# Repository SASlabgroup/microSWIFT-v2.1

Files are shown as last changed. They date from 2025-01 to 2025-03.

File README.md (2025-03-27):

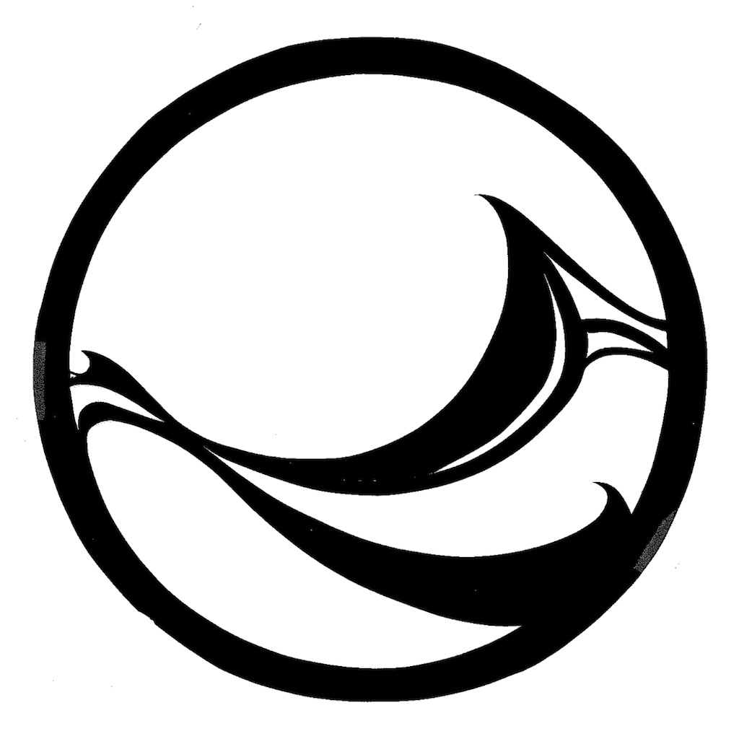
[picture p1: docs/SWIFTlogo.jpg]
#  microSWIFT v2.1

Static repository for documentation, source code, and CAD files for version 2.1 of the microSWIFT wave buoy.

## About microSWIFT
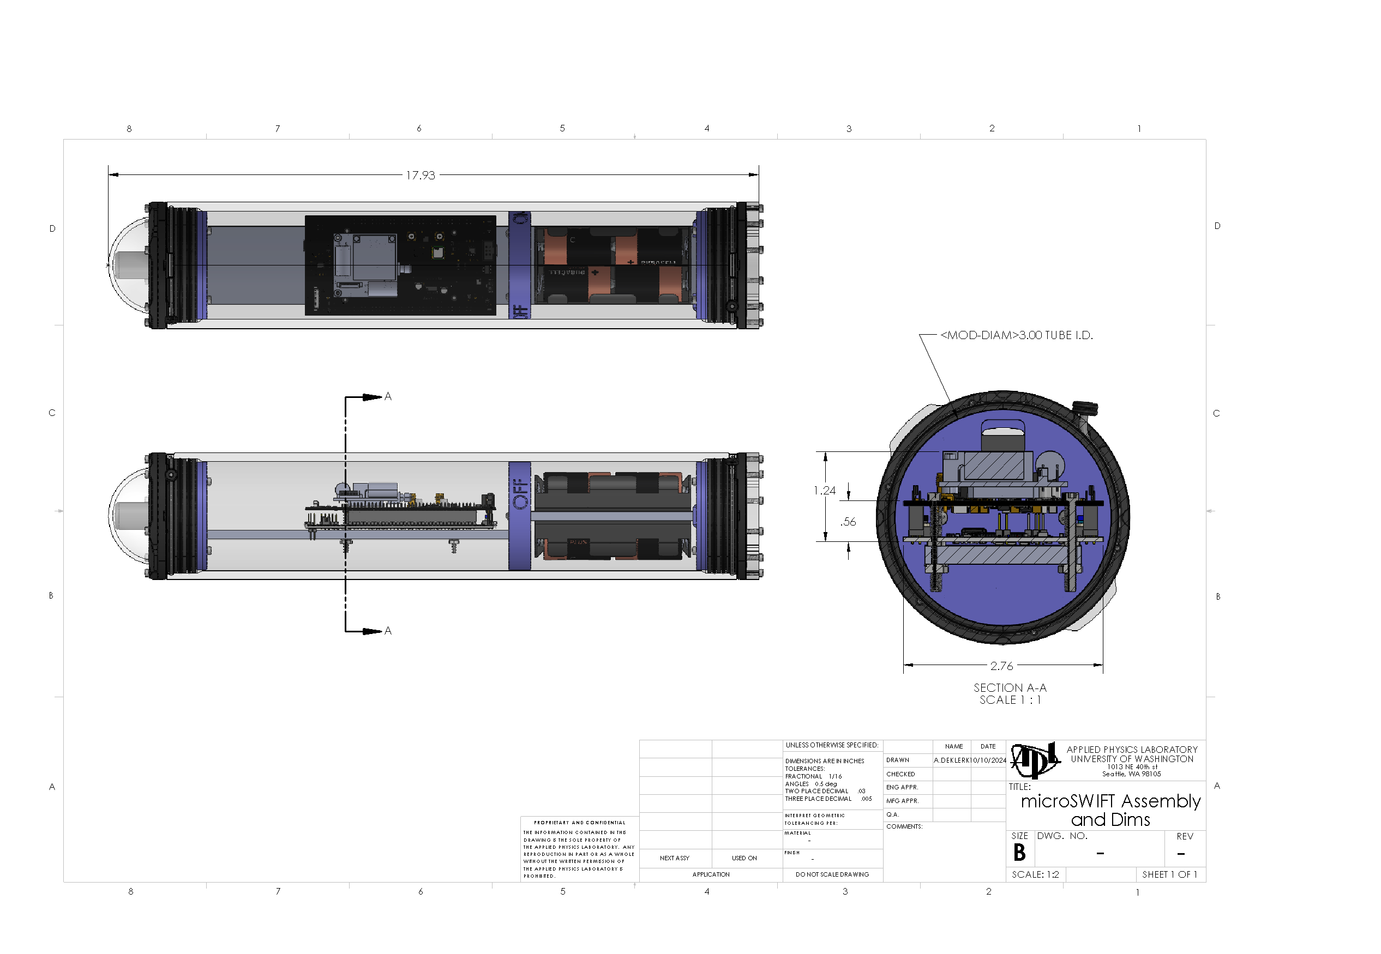
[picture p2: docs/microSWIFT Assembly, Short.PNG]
# 
microSWIFT is a low-cost, expendable, freely drifting wave buoy built by at the UW Applied Physics Lab.  It uses the Iridium satellite network to report real-time ocean wave data. It also supports additional measurements such as surface salinity and temperature via auxiliary sensors.

microSWIFT can be deployed from an aircraft through a standard A-size Sonobuoy tube.  This makes it ideal for collecting wave data in environments not accessible by ship, such as in the path of a hurricane or in polar regions.  It can also be deployed by hand over the side of a ship like a traditional buoy or drifter.

The name microSWIFT owes to the fact that it is a miniaturized version of a SWIFT wave drifter.  SWIFT is an acronym for Surface Wave Instrument Float with Tracking.

Visit the main APL project page for more information: https://apl.washington.edu/swift

Database (real time and archive) is available here: https://faculty.washington.edu/jmt3rd/SWIFTdata/DynamicDataLinks.html

A full Python package for working with microSWIFT  telemetry data is available as a separate repository: 
https://github.com/SASlabgroup/microSWIFTtelemetry

The microSWIFT v2 onboard software is here: https://github.com/SASlabgroup/microSWIFT-V2

## microSWIFT v1
The first version of the microSWIFT was based on a Raspberry Pi Zero and ran on Python code.  Documentation and operational code can be found a the microSWIFT v1 repo: 
https://github.com/SASlabgroup/microSWIFT

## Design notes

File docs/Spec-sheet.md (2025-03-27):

# Specs and Features

# 
## General Specifications

|                                       |                                                |
|:------------                          |:-----------------------------------------------|
|Enclosure                              |Acrylic watertight housing (120 m depth rating)
|Buoy dimensions                        |3.5 in diameter, 17.9 in length
|Weight                                 |6 lbs
|Air-drop package                       |Cardboard tube with 28” diameter chute
|Air-drop dimensions                    |4.25” diameter, 25.5” length,
|Air-drop weight                        |8 lbs (including buoy)
|Batteries                              |8 standard Alkaline “C” cells, user replaceable
|Endurance                              |21 days
|Telemetry                              |Satellite (Iridium SBD), 9603 modem
|Processor                              |STM32U5 series (ARM® Cortex®-M33) , 768 kB RAM, 2048 kB Flash memory
|Onboard software                       |C (https://github.com/SASlabgroup/microSWIFT-v2.1-source)
|Duty cycle                             |Configurable.  Typically 30 minute interval for collection of raw wave data (GPS at 4 Hz), onboard processing, and telemetry.  
|Optional sensors                       |Conductivity and temperature (CT) sensor
|Optional long endurance configuration  |16x C cell batteries in extended housing

## Data Products
|                                                     |                                                |
|:------------                                        |:-----------------------------------------------|
|Position (lat, lon)                                  |± 5 m
|Significant wave height, Hs                          |± 0.1 m
|Peak wave period, Tp                                 |± 1 s
|Dominant wave direction, Dp                          |± 15 deg
|Scalar wave energy spectrum, E(f)                    |± 10-2 m2/Hz, 0.05 < f < 0.5 Hz
|Directional moments of the spectrum (a1,a2,b1,b2)    |± 0.1, 0.05 < f < 0.5 Hz

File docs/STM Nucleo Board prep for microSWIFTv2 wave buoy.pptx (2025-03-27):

## STM NUCLEO Board prep for microSWIFT v2 wave buoy

(NUCLEO-U575ZI-Q)
Alex de Klerk, Aug 2023

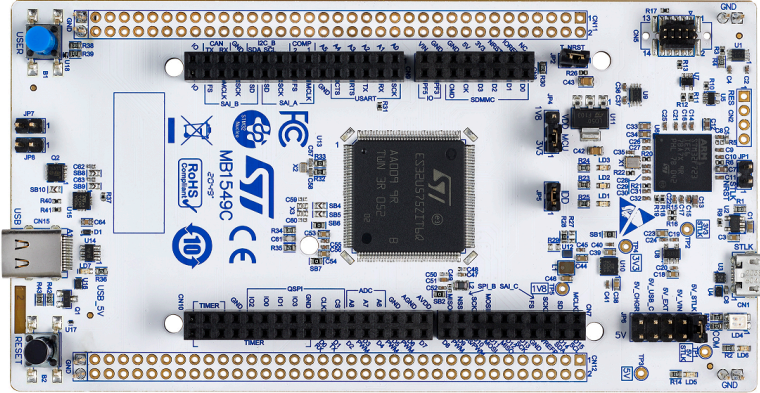
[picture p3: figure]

## Follow ESD safe practices while handing electronic circuit board and components

- Use an ESD safe work mat that is grounded
- Wear grounding strap
- Store board in factory anti-static bag

## 1) Flush cut header pins

- Remove board from packaging
- Use good flush cutters (Knipex or similar)
- Trim header pins on bottom side of board flush with board (red boxes)
- Be careful not to damage silk screen or traces

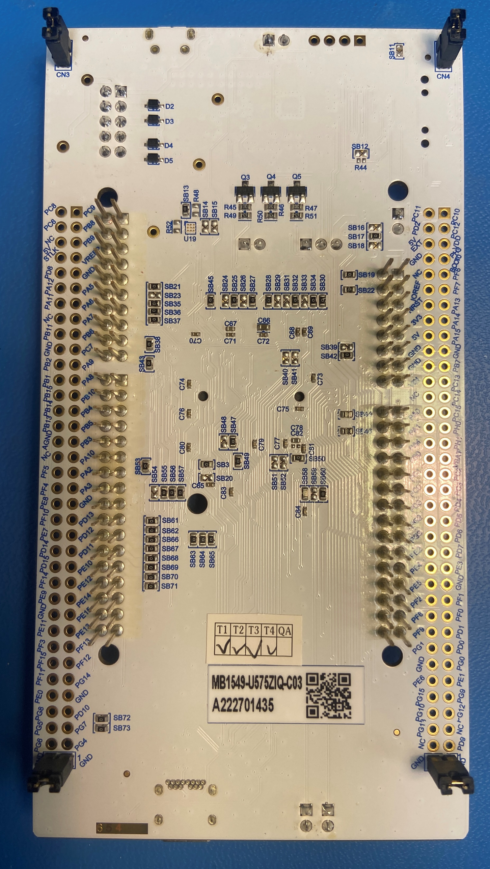
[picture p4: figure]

## 2) Solder male header pins

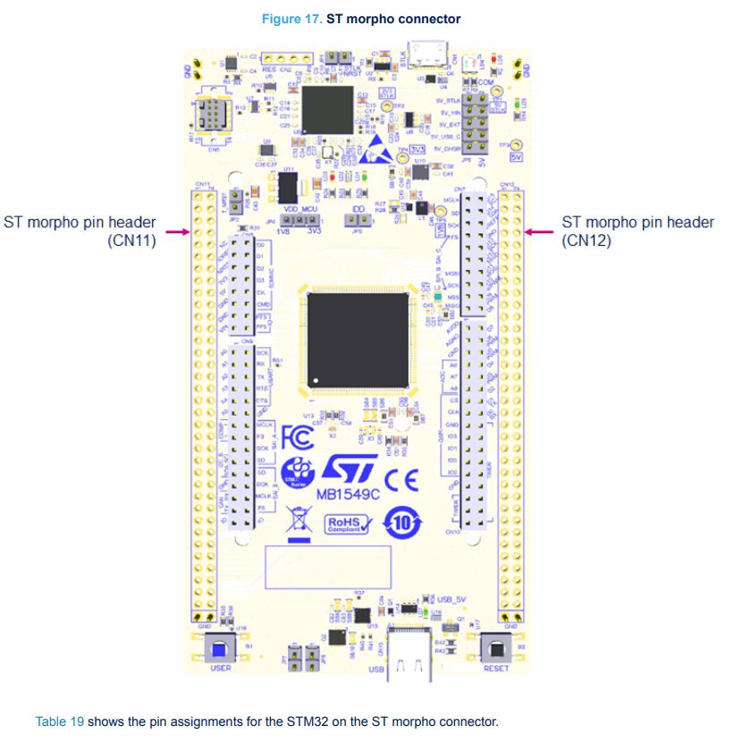
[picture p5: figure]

- Use 2x35 male header pins, qty 2
- Solder on top side of board in MORPHO locations (outer 4 rows) as shown below
- Use flux and make sure flows between pad and header pin

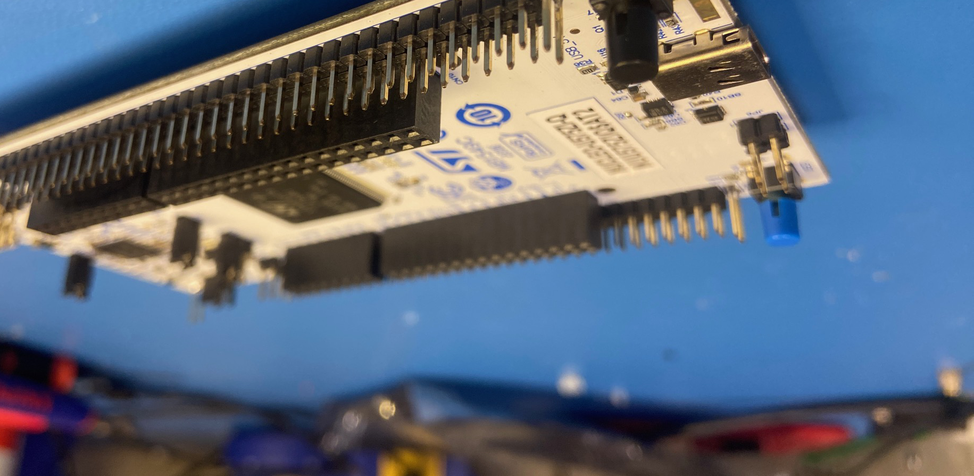
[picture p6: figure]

## 3) De-populate SB1

- Remove 0 Ohm resistor from SB1 location
- Use solder wick and flux to remove excess solder

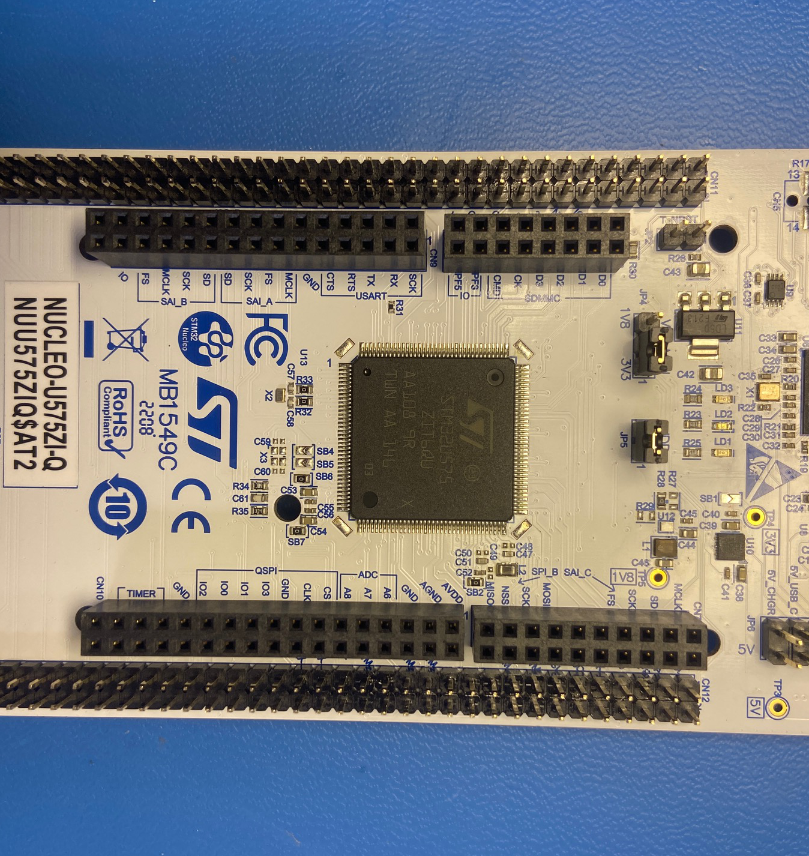
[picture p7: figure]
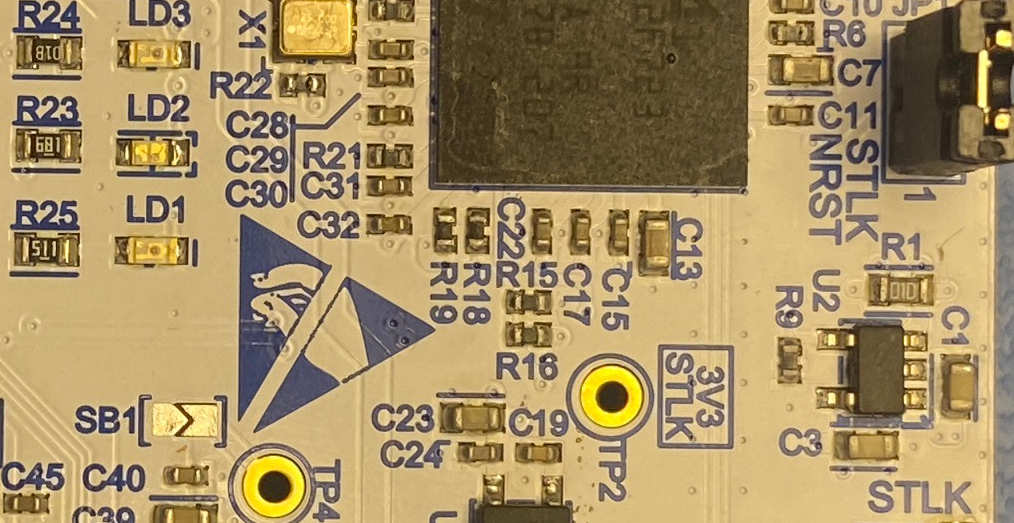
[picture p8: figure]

SB1

## 4) De-populate SB3

- Remove 0 Ohm resistor from SB3 location (bottom side)
- Use solder wick and flux to remove excess solder

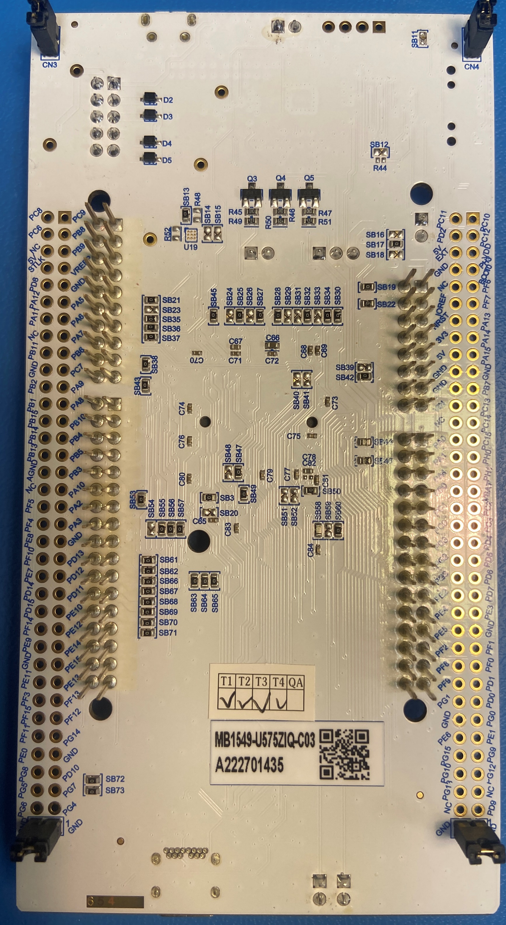
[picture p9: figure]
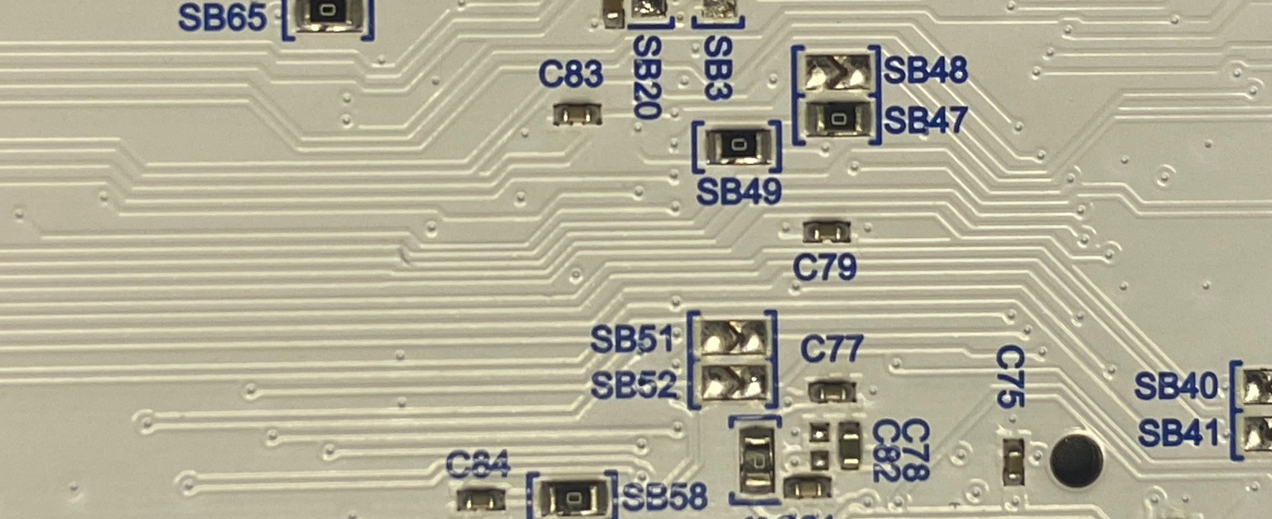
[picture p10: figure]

SB3

## Set Jumpers

- Remover jumper JP6
- Remove jumper JP2
- Install jumper at JP1

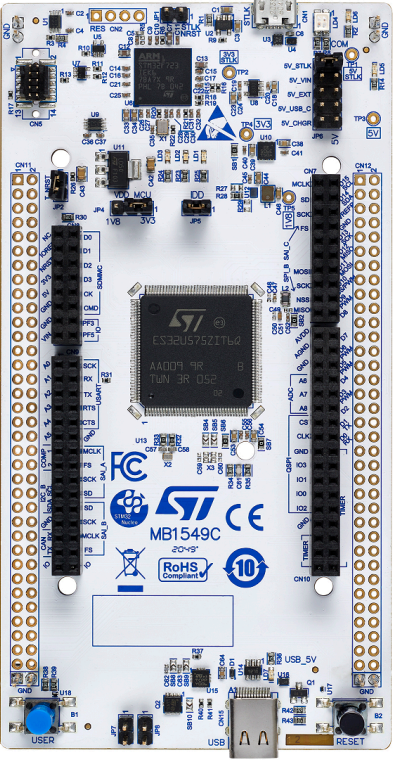
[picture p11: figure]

## 5) Clean flux from board

- Use isopropyl alcohol (IPA) in a squirt bottle and a stiff brush (ESD safe preferable)
- Wet board with IPA and scrub flux at all solder locations, SB1, and SB3
- Rinse and scrub several times
- Final rinse and air dry with canned compressed air

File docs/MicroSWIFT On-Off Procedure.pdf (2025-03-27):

# MicroSWIFT On/Off Procedure

## To Turn on the microSWIFT

The microSWIFT can be turned on by placing a magnet wand or other magnet near the location marked ‘ON’ for 1-3 seconds. The magnet sensor is located in the bottom right corner of the circuit board.

When powered on, a red and green status LEDs will alternately flash while the microSWIFT boots up. After approximately 1 minute, there should be a solid green LED, indicating the microSWIFT has started running successfully.

During operation, there will be a solid green LED while the buoy is collecting data, otherwise both status LEDs will be off.

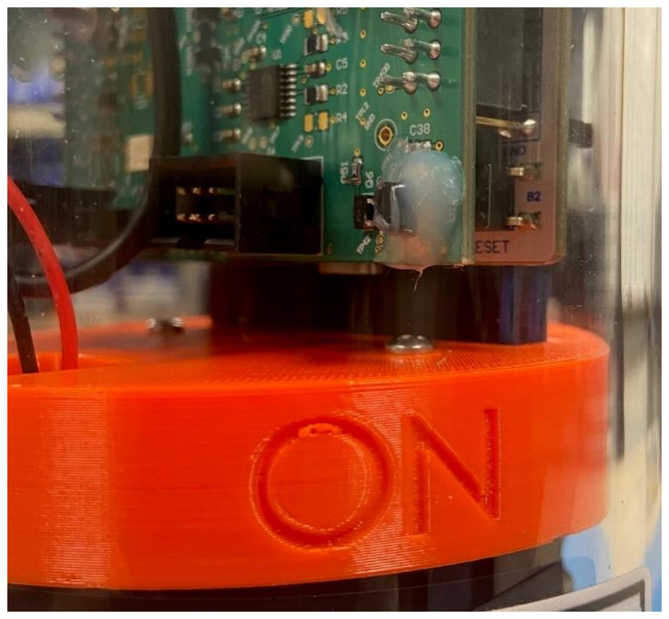
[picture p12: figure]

## To Turn off the microSWIFT

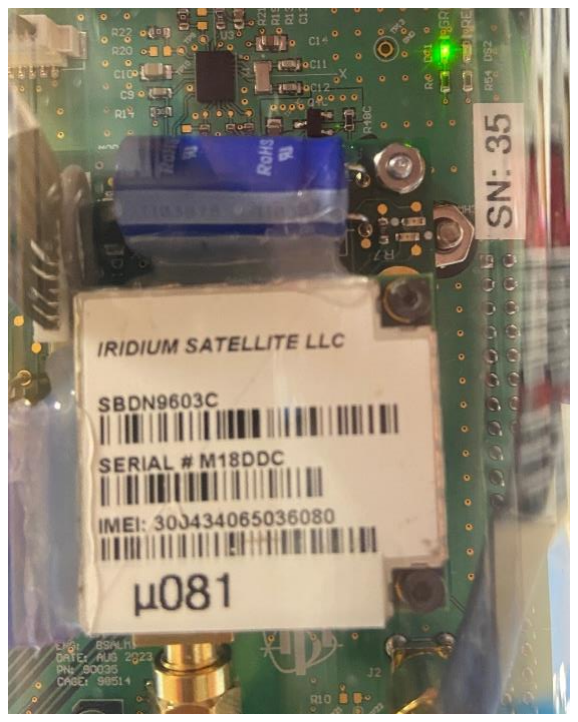
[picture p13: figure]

Place the magnet wand or another magnet near the location marked ‘OFF’. The status LEDs will turn off, however the LEDs on the Iridium modem will turn on as its capacitor discharges.

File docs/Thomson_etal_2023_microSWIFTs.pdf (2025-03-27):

Full Terms & Conditions of access and use can be found at https://www.tandfonline.com/action/journalInformation?journalCode=tcej20

Jim Thomson, Phil Bush, Viviana Castillo Contreras, Nate Clemett, Jacob

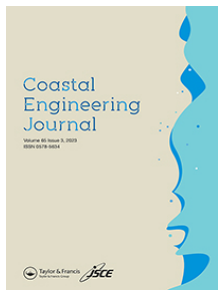
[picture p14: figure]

Davis, Alex de Klerk, Emily Iseley, Edwin James Rainville, Brenton Salmi & Joe Talbert (22 Nov 2023): Development and testing of microSWIFT expendable wave buoys, Coastal Engineering Journal, DOI: 10.1080/21664250.2023.2283325 (https://www.tandfonline.com/action/showCitFormats?doi=10.1080/21664250.2023.2283325)
https://doi.org/10.1080/21664250.2023.2283325

© 2023 The Author(s). Published by Informa UK Limited, trading as Taylor & Francis Group.

Published online: 22 Nov 2023.

Submit your article (https://www.tandfonline.com/action/authorSubmission?journalCode=tcej20&show=instructions) to this journal

View related (https://www.tandfonline.com/doi/mlt/10.1080/21664250.2023.2283325) articles

View Crossmark (http://crossmark.crossref.org/dialog/?doi=10.1080/21664250.2023.2283325&domain=pdf&date_stamp=22%20Nov%202023) data

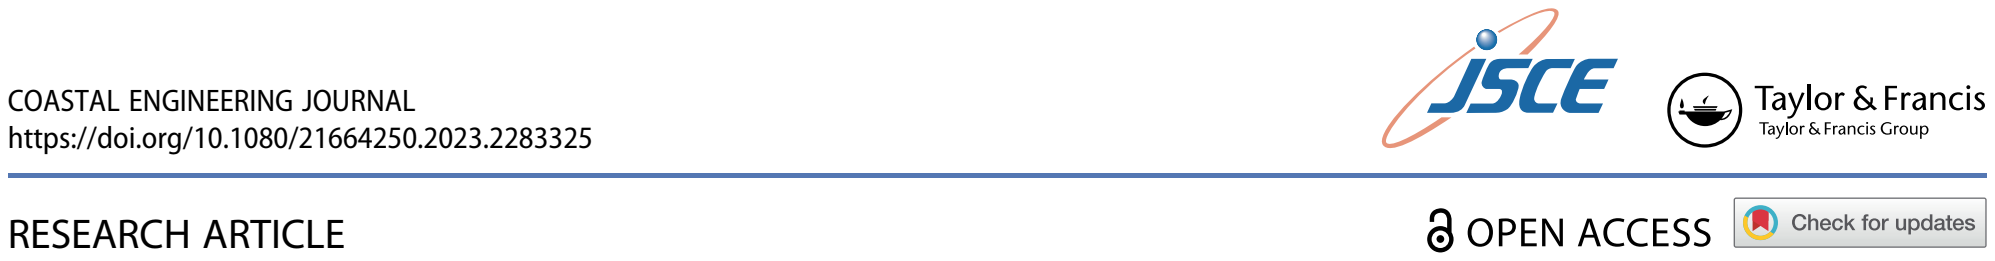
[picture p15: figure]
RESEARCH ARTICLE; COASTAL ENGINEERING JOURNAL https://doi.org/10.1080/21664250.2023.2283325

## Development and testing of microSWIFT expendable wave buoys

Jim Thomson , Phil Bush, Viviana Castillo Contreras, Nate Clemett, Jacob Davis , Alex de Klerk, Emily Iseley, Edwin James Rainville , Brenton Salmi and Joe Talbert

Applied Physics Laboratory, University of Washington, Seattle WA, USA

ABSTRACT
Expendable microSWIFT buoys have been developed and tested for measuring ocean surface waves. Wave spectra are calculated via onboard processing of GPS velocities sampled at 5 Hz, and wave spectra are delivered to a shore-side server via Iridium modem once per hour. The microSWIFTs support additional sensor payloads, in particular seawater conductivity and temperature. The buoys have a non-traditional, cylindrical shape that is required for deployment via the dropsonde tube of research aircraft. Multiple versions have been developed and tested, with design considerations that include: buoy hydrodynamics, sensor noise, algorithm tuning, processor power, and ease of deployment. Field testing in a range of conditions, including near sea ice and in a hurricane, has validated the design.

ARTICLE HISTORY
Received 9 July 2023
Accepted 30 October 2023
Published online
KEYWORDS
Ocean surface waves; wave
buoy; wave measurements;
wave spectra

### 1. Introduction

The modern era of ocean wave measurements is de!ned by an expansion in operational remote sensing (e.g. satellite altimeters, lidar scanners) and by a "ood of inexpensive wave buoys (e.g. Spotter buoys, openMet buoys). Amidst the plethora of miniature wave buoys, one can and should ask if another wave buoy is needed. The answer is that speci!c projects often require unique features or sampling modes not available in existing buoy designs. Our development of microSWIFT buoys has been motivated by several speci!c projects needs, including: access to raw data for phase resolved models, high sampling rates for breaker detection, robustness in sea ice, aerial deployment from the dropsonde tube of research aircraft, and inclusion of additional sensors as modular payloads. Collins et al. (2024) provides a thorough review of wave buoy measurements and an inter-calibration e#ort for several miniature wave buoys. Much of this activity traces directly back to Herbers et al. (2012), who demonstrated the utility of Global Positioning System (GPS) Doppler velocities as the raw motion data for wave spectral analysis. This was a departure from the classic pitchroll-heave motion data (Kuik, Van Vledder, and Holthuijsen 1988), and thus the use of GPS data helped launch a new generation of wave buoys. The SWIFT buoys (Thomson 2012) immediately adopted the GPS approach, as did many other buoys and platforms (Raghukumar et al. 2019; Thomson et al. 2018). Other modern buoys have used newly available, low-cost Inertial Motion Unit (IMU) sensors (Feddersen et al. 2024; Rabault et al. 2020, 2022). The development of microSWIFT buoys has explored both GPS and IMU approaches, as part of a larger e#ort to miniaturize the original SWIFT design and end up with something compact and expendable.
The goal of this paper is to describe the development and testing of microSWIFT buoys, with particular attention to lessons learned that have steadily improved the quality of the wave data and the usability. Section 2 describes the design of the buoys, Section 3 describes the algorithms, Section 4 describes testing the buoys, and Section 5 summarizes the deployments to-date.

### 2. Buoy design

There have been three versions of microSWIFT buoys to date, each with a few variations. The !rst beta version was a simple proof-of-concept. Subsequent versions have evolved to address weaknesses identi!ed during testing and to address new mission requirements associated with new research projects. Figure 1 shows the di#erent physical designs, and Table 1 summaries the speci!cations. The choice of a cylindrical buoy shape throughout all versions, rather than the more common spherical buoy shape, is driven by a requirement for aerial deployments using the A-sized tube (nominal 5-inch diameter) for dropsondes from research aircraft, such as the NOAA P-3 Hurricane Hunter or Twin Otter.

CONTACT J. Thomson. jthomson@apl.washington.edu
© 2023 The Author(s). Published by Informa UK Limited, trading as Taylor & Francis Group.
This is an Open Access article distributed under the terms of the Creative Commons Attribution-NonCommercial-NoDerivatives License (http://creativecommons.org/licenses/bync-nd/4.0/), which permits non-commercial re-use, distribution, and reproduction in any medium, provided the original work is properly cited, and is not altered, transformed, or built upon in any way. The terms on which this article has been published allow the posting of the Accepted Manuscript in a repository by the author(s) or with their consent.

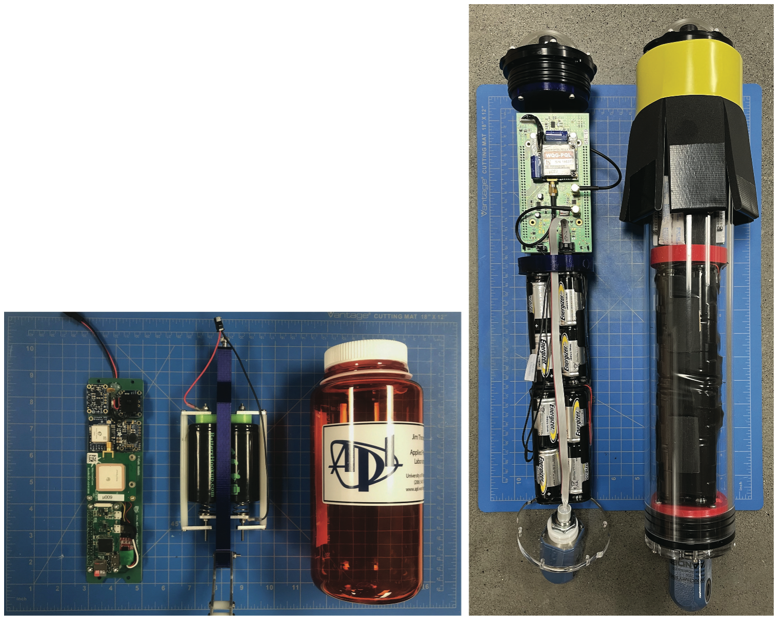
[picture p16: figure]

### 2.1. microSWIFT v-beta

The beta version of the microSWIFT buoy was simply a 1-Liter, Naglene-brand water bottle with two commercial, o#-the-shelf components: a GPS logger (Qstarz) and a dog-tracking collar (Garmin Astro). These were !rst deployed in 2014 to measure the wakes of Washington State Ferries in Rich Passage (Perfect et al. 2015), and later used for the DUNEX pilot in 2019. The endurance was approximately one day, and the system had no onboard processing or telemetry. The buoys had to be recovered (based on tracking with the dog collars) and the raw GPS data o$oaded for post-processing.

### 2.2. microSWIFT v1 (1-L and 2-L)

The !rst production version of the microSWIFT buoy still uses the 1-Liter Naglene bottle as the housing and upgrades the electronics to a RaspberryPi-0 processor on a custom Printed Circuit Board (PCB). This enables integration of a GPS receiver and IMU, with onboard processing and telemetry of results via Iridium modem. The RPi processor is an excellent choice for rapid, collaborative software development. A set of Python codes, managed in a public GitHub repo (https://github.com/SASlabgroup/microSWIFT) (https://github.com/SASlabgroup/microSWIFT) controls all aspects of data logging, processing, and telemetry. The RPi is also an excellent choice for short-deployments, because the WiFi connectivity can be used to automate the o$oad and organization of raw data from a large number of buoys (once recovered and in range of the network). This was helpful during the DUNEX main experiment, when up to 50 buoys were deployed on daily missions and post-processing raw data was essential (Rainville et al. 2023).
The RPi is a less ideal choice in terms of power usage. The v1 buoys use approximately 200 mW on-average, and most of this is the RPi itself (as opposed to the GPS, IMU, or Iridium modem). For the 1-L Naglene bottle housing with two D-cell rechargeable batteries, the maximum mission life is two days. A 2-L housing, based on Blue Robotics 3-inch inner diameter pressure

Figure 1. microSWIFT versions. Left: v1 in a 1-L Naglene bottle housing. Right: v2 in a 2-L housing (also used in a variation of v1) with an octopus foam collar. The 2-L version has an optional conductivity-temperature (CT) sensor at the bottom of the housing.

Table 1. microSWIFT versions.
Version | Processor | Endurance | Housing | Code base | Tracking/Telemetry | Unit Cost
beta | none | 1 day | 1-L Naglene | none | Dog collar/none | $250
v1 | RaspberryPi-0 | 2 days | 1-L Naglene | Python | Iridium | $500
v1 | RaspberryPi-0 | 5 days | 2-L Blue Robotics | Python | Iridium | $600
v2 | STM | 30 days | 2-L Blue Robotics | C | Iridium | $900*
*cost is increased by $2,000 with optional CT sensor.

2 J. THOMSON ET AL.

cases, provides space for 16 C-cell batteries and extends mission life to !ve days. This has been essential for successful deployments during the !rst year of the NOPP Hurricane Coastal Impacts (NHCI) program (see Section 5). The 2-L housing also includes a dedicated GPS antenna that improves the quality of the GPS velocities.

### 2.3. microSWIFT v2

The second production version of the microSWIFT replaces the RaspberryPi with a low-power microprocessor (STM32). This increases the endurance to approximately 30 days with the same 2-L housing and 16 Alkaline C-cell batteries. The increased endurance enables persistent observing that can capture events, especially in the western Arctic and in the tropical Atlantic pathway for hurricanes (see Section 5). The switch to a microprocessor includes a switch to C as the codebase and more specialized/intensive software development. Compared with the numerous Python libraries available for the RPi on v1, much of the C software for v2 had to be developed from scratch.
The v2 microSWIFT upgrades the GPS receiver to a multi-constellation GNSS unit (UBlox M10) which tracks up to 32 satellites at a time, compared with 16 GPS satellites tracked by most consumer grade GPS receivers. The additional satellites tracked are from the GALILEO, GLONASS, and BEIDOU constellations in orbit. The additional satellites improve the accuracy of the velocity components used as inputs to the onboard wave processing (Section 3), especially the vertical component of velocity. Errors in velocity components are expected to be <0:05 m/s. The v2 microSWIFT has a new PCB to integrate the microprocessor, GNSS receiver, and Iridium modem. Provisions for an IMU exist, though it is not included in the present onboard processing (see Section 3). There is also magnetic power switch, such that it can be turned on without opening the pressure case or the air-deployment rigging. The v2 microSWIFT also includes a conductivity and temperature (CT) sensor (Aanderaa 4319) at the bottom of the 2-L hull for determination of sea surface salinity and sea surface temperature (approximate measurement depth 0.2 m). This continues a general modular sensor approach used in the original full-scale SWIFTs, which have supported the same model CT for years (along with acoustic Doppler pro!lers, meteorological sensors, cameras, "uorometers, etc).

### 3. Onboard data processing

This section describes the microSWIFT onboard processing of GPS data to produce the standard ocean wave spectral and bulk metrics. Testing of the v1 microSWIFT included several iterations using the IMU data to produce similar metrics, as done on some other mini buoys (Feddersen et al. 2024; Rabault et al. 2020, 2022). Although post-processing the IMU data produced excellent results from the DUNEX project (Rainville et al. 2023), it has not been adopted as the standard for onboard processing. Two key problems have prevented the use of IMU data for onboard processing: 1) the correction from the body reference frame to the earth reference frame, and 2) the introduction of spurious energy at low frequencies when integrating motion data to estimate position. Both of these problems can be solved with su%cient computational power, !ltering, and calibration.
Rather than implement IMU sensor-fusion algorithms onboard or rely on black-box state estimates, we have chosen to use the GPS velocities exclusively in the onboard processing. These velocities are agnostic to buoy orientation and already in an earth reference frame, with orthogonal north-eastdown components (v; u; w). This approach is particularly well suited to non-spherical shapes that may not follow surface slopes. The processing uses the frequency spectra SÖfÜ of the components to estimate the scalar energy spectra,

## EÖfÜ à SuuÖfÜ á SvvÖfÜ

Ö2πfÜ

2 | (1)

and the standard directional moments,
a1ÖfÜ à | ImÖSuwÜ ÅÅÅÅÅÅÅÅÅÅÅÅÅÅÅÅÅÅÅÅÅÅÅÅÅÅÅÅÅÅÅÅÅÅÅÅÅÅÅÅÅÅÅÅÅÅ ÖSuuÖfÜ á SvvÖfÜÜSwwÖfÜ p | ;
b1ÖfÜ à | ImÖSvwÜ ÅÅÅÅÅÅÅÅÅÅÅÅÅÅÅÅÅÅÅÅÅÅÅÅÅÅÅÅÅÅÅÅÅÅÅÅÅÅÅÅÅÅÅÅÅÅ ÖSuuÖfÜ á SvvÖfÜÜSwwÖfÜ p | ;

(2)

## a2ÖfÜ à SuuÖfÜ SvvÖfÜ SuuÖfÜ á SvvÖfÜ

; b2ÖfÜ à 2ReÖSuvÖfÜÜ
SuuÖfÜ á SvvÖfÜ (3)

For more information and diagrams interpreting the directional moments a1; b1; a2; b2, see the appendix of Thomson et al. (2018). The use of horizontal velocities in Eq. 1 assumes circular orbits in deep water. This assumption could be relaxed by the use of vertical velocities, which have the same f 2 relation to sea surface spectra in any water depth. However, the vertical velocities tend to have higher levels of noise, and thus are not preferred. The assumption of circular orbits is evaluated with another spectral quantity that is calculated onboard, which is the ratio of vertical to horizontal motion known as the check factor
check ÖfÜ à SwwÖfÜ

## SuuÖfÜ á SvvÖfÜ

: | (4)

This should be equal to one in deep water. Note that energy spectra EÖfÜ derived from horizontal velocities with a deep-water assumption can be

COASTAL ENGINEERING JOURNAL 3 adjusted for intermediate water depth (if known) by using the linear dispersion relation.
The onboard processing code was developed in Matlab and the source is included the public SWIFTcodes GitHub repository (https://github.com/SASlabgroup/SWIFT-codes/waves/NEDwaves. m). (https://github.com/SASlabgroup/SWIFT-codes/waves/NEDwaves.m) For the v1 microSWIFTs, this was translated to Python. For the v2 microSWIFTs, this was built as a C static library using the Matlab Coder application. Building the C library required some changes to improve memory management, which is not optimized in the Matlab code conversion.
Each 30-minute burst of raw GPS data is processed in windows of 256 s each, with 75% overlap. Prior to an FFT, each window is prepared with a high-pass RC !lter to remove drift from the velocities and a variance-preserving cosine taper to remove edge e#ects. The RC !lter is the same as Thomson et al. (2018), where the time constant is set as 4 ⇥ 2π ⇡ 25 seconds as the longest period retained in the raw time series data. The resulting ensemble spectra have 16 degrees of freedom (from 8 independent windows). This is then increased to 48 degrees of freedom by merging every three neighboring frequency bands. The frequency-band merging also reduces the total size of the !nal spectrum for telemetry.
Standard bulk parameters are calculated onboard, including signi!cant wave height

# Hs à 4 ÅÅÅÅÅÅÅÅÅÅÅÅÅÅÅÅÅÅ

P Å EÖfÜdf p , peak wave period Tp, and peak wave direction Dp. Other parameters are readily calculated from the onboard spectra, including the energy-weighted centroid period Te and the mean square slope mss.

### 3.1. Telemetry

A key feature of any expendable system is the telemetry of data products, since the raw data will not be recovered. The microSWIFTs use an Iridium Short Burst Data (SBD) modem (model 9603B). The processed wave spectra meta data are assembled onboard as byte arrays and sent in a single binary SBD packet (limit: 340 bytes). This uses half-"oat precision values to be able to !t all !ve spectra moments. The custom formatting of this binary packet is readable in Python ( https://github.com/SASlabgroup/microSWIFTtelemetry/blob/main/microSWIFTtelemetry/sbd/read_sbd.py) (https://github.com/SASlabgroup/microSWIFTtelemetry/blob/main/microSWIFTtelemetry/sbd/read_sbd.py) or Matlab (https://github.com/SASlabgroup/SWIFT-codes/blob/master/GeneralTools/readSWIFT_SBD.m). (https://github.com/SASlabgroup/SWIFT-codes/blob/master/GeneralTools/readSWIFT_SBD.m)
A shore-side server at APL-UW receives these SBD packets as e-mails and parses them with a Python script. The script populates a database hosted on the server, which is then accessed with an API (Application Protocol Interface). The API is a public interface, which queries the server by building urls for speci!c buoys, data formats, and times. The API can be queried in a variety of automated modes (curl, wget, etc), and there no di#erence between the public API and the access of internal APL-UW users. A Python package (https://github.com/SASlabgroup/microSWIFTtelemetry) and a Matlab function (https://github.com/SASlabgroup/SWIFT-codes/blob/master/GeneralTools/pullSWIFTtelemetry.m) (https://github.com/SASlabgroup/SWIFT-codes/blob/master/GeneralTools/pullSWIFTtelemetry.m) are available to work directly with the API. There also is a simple user interface at the data tab of www.apl.uw.edu/swift for accessing data directly via a web browser. A live map showing buoys and data on a rolling three-hour window is also available.

### 4. Initial buoy testing

Prior to !eld deployments, the buoys are tested to determine: 1) the sensor noise using static tests, 2) the hydrodynamic response using free decay oscillations in a tank, and 3) the motion signals on a rotary test stand. In additions, a series of aerial deployment tests determined the rigging required for the buoys to survive aircraft deployments.

### 4.1. Static noise

The !rst test for each microSWIFT version is to record a burst of raw data without motion and evaluate the sensor noise. Quanti!cation of sensor noise is particularly important for wave buoys intended for deployment in ice, because even modest noise levels can a#ect the spectral energy ratios used to calculate wave attenuation by sea ice (Thomson et al. 2021). The static test can be done as part of a bench test, but only if the bench location has su%cient GPS signal. A typical burst of raw data is 2048 seconds long and sampled at 4 Hz. The onboard processing of this data produces an empirical noise spectrum, along with an e#ective noise height Hn. This is only a proxy for uncertainty in the operational wave results, as the sensor noise and buoy dynamics in a given sea state might di#er from the static tests. Still, it is a useful check-point in the development process.
Figure 2 shows the noise spectra EnÖfÜ from both v1 and v2 buoys. The spectra have an expected f 2 shape, which results from white noise (f ⁰) in velocity that is converted to elevation (equation 1). These spectra can be integrated to obtain an equivalent noise level in signi!cant wave height, which is generally less than 0.1 m. The v2 buoys have a higher (worse) noise "oor, and work is ongoing to reduce this noise. A parallel approach is to remove the noise by simple subtraction of the empirically determined static noise spectrum EnÖfÜ from each observed wave spectrum EÖfÜ, assuming that the noise is

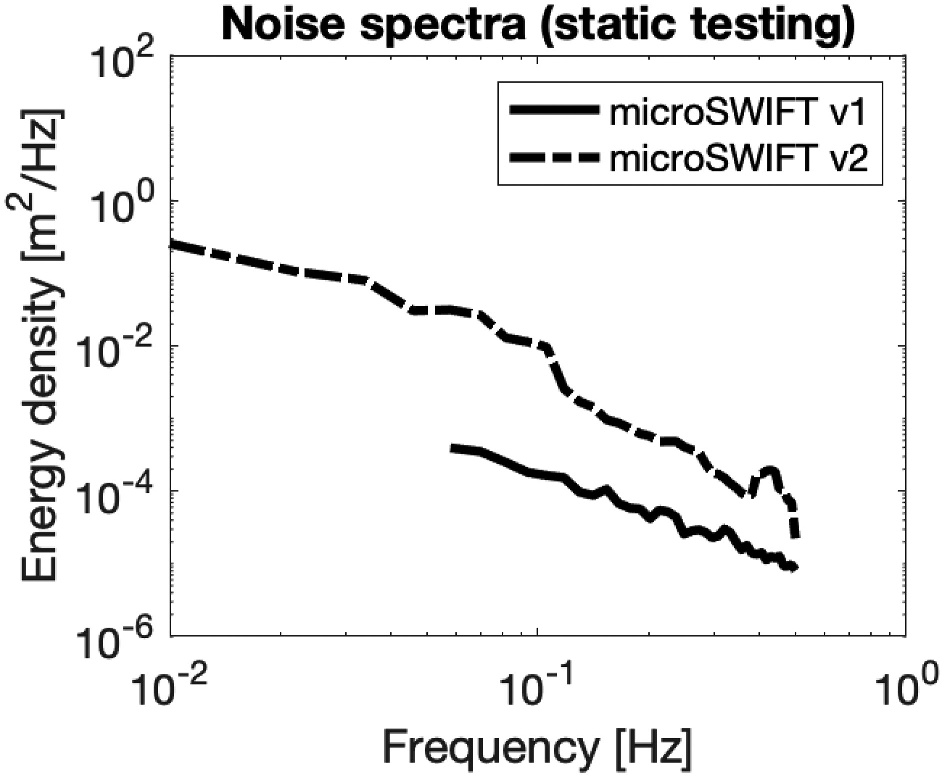
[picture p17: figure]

uncorrelated from the signal (see Thomson et al. (2021) for discussion of noise super-position). This is promising, though not yet implemented in the operational version of the onboard software.
The increased noise likely is related to the di#erent GPS (or rather, GNSS) receivers, though it could also be the antennas. MicroSWIFT v1 uses a GlobalTop receiver (model FGPMMOPA6H) and an active patch antenna. MicroSWIFT v2 uses a UBlox receiver (model MAX-M10S) and a passive cylindrical antenna, which is shared with the Iridium modem. Although the UBlox is nominally a higher-quality sensor, the noise in the velocity measurements is clearly higher. One possibility is multi-pathing of the GNSS signal caused by the metal ring of the buoy end-cap. However, removing the end-cap during static testing (on land) does not reduce the noise. It is possible that the addition of a grounding plane would help the antenna performance; we plan to try this in a future version. Though the noise is clearly worse for v2, it is still a relatively small e#ect on signi!cant wave height (,0:1 m).

### 4.2. Free decay oscillations

The heave response of any "oating body can be described as a mass-spring-damper oscillation, which then determines the natural frequency fn at which the body will bob,
fn à 1
2π

# ÅÅÅÅÅÅÅÅÅÅÅ ρwgV

ML r
: | (5)

The buoyancy force is determined by the density of the water ρw, gravity g, and the displaced volume V. The mass M and vertical length (draft) L control the inertia. For a spar, the ratio V=L simpli!es to πr

2, and the
resulting fn does not depend on the draft of the buoy. The denominator often includes a term for added mass in addition to the actual mass. This is the water surrounding the buoy that is accelerated with the buoy, and it is usually characterized with an added mass coe%cient multiplied by the displaced volume of water. For small objects the added mass adjustment is often negligible. The physical heave added mass of a spar, Aheave à ²
3 πρwr

3, for the 2-L hull with radius r à 4:45 cm is 0.2 kg, is about 5% of the buoy’s mass. For a wave buoy, the ideal design is a natural frequency that is above the energetic frequencies of ocean waves (nominally 0:05<f <0:5 Hz), such that the buoy has an sti# response to the wave motion. Prior work has shown reduction in buoy response with increasing buoy mass when the natural frequency decreases enough to fall within the wave bands (Thomson et al. 2015). The 1-L microSWIFT has fn à 2:00 Hz and the 2-L microSWIFT has fn à 0:75 Hz. Both meet the nominal requirement for fn to be greater than the wave frequencies of interest, but that alone does not guarantee buoy performance. The mass, geometery, and theoretical natural frequency of each version are in Table 2. The 2 L designation is a clear misnomer, relative to displaced volume of the buoy, but we retain the name here for legacy reasons and continuity of design documents.
A more comprehensive approach to buoy response is to determine a frequency-dependent Response Amplitude Operator (RAO) for the buoy, based on the response to known forcing. This is rarely uniform in frequency. Instead, it has a resonant peak at the natural frequency (equation 5) and increasing damping away from this frequency. The damping is generally far more severe for f >fn, hence the requirement for fn to be greater than the wave frequencies of interest. A simple test of both the natural frequency and the RAO is a free decay oscillation, in which the buoy is submerged completely (or dropped) and then allowed to respond without additional forcing. Figure 3 shows the free decay of a 2-L buoy, in which the empirical fn,0:77 Hz con!rms the calculated fn,0:75 Hz calculated and shows the damping at frequencies above and below fn. For the v1-2 L version, damping of resonance at fn is achieved with a "otation collar that has six

Figure 2. Energy spectra from static noise testing of buoys.

Table 2. microSWIFT mass and geometry.
Version | Orientation | Mass | Length | Diameter | Displaced volume | Natural frequency
v1-1L | horizontal | 0.9 Kg | 21.4 cm | 9.2 cm | 1.4 L | 2.00 Hz*
v1-2L | vertical | 2.8 Kg | 48.3 cm | 8.9 cm | 3.0 L | 0.75 Hz
v2-2L | vertical | 2.9 Kg | 51.0 cm | 8.9 cm | 3.2 L | 0.74 Hz
*In a vertical configuration, the 1L microSWIFT would have fn à 1:38 Hz.

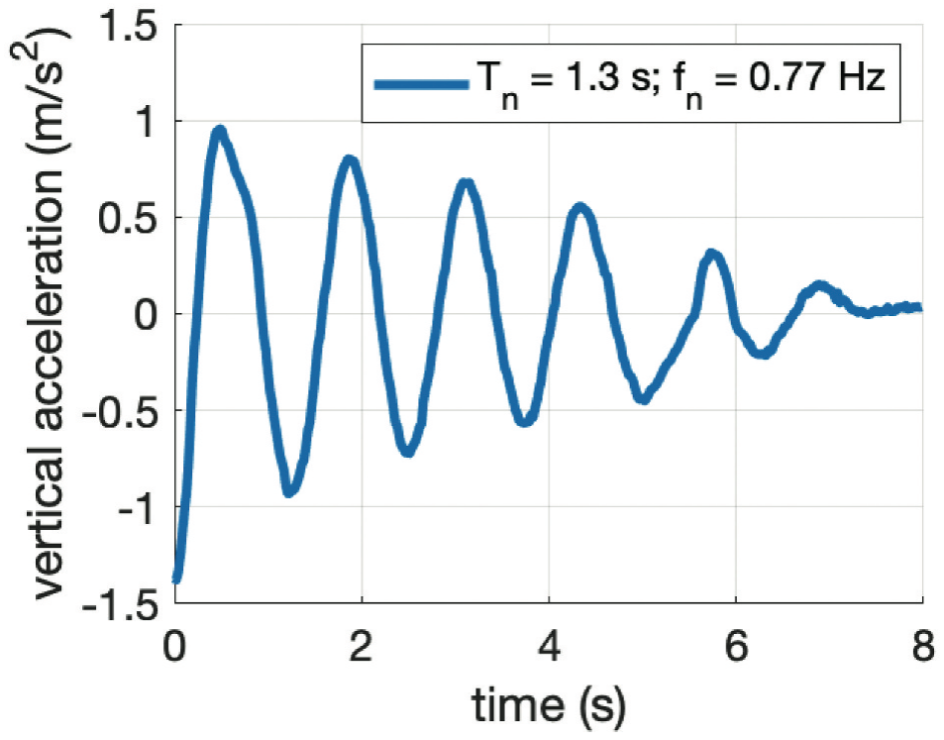
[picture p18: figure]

independent "aps we call the octopus collar¹ The octopus collar uses strips of closed-cell foam that are 2 inches wide and 0.25 inches thick. The six strips are placed lengthwise along the upper hull, then the tops of all strips taped in circumference (see yellow tape banded around the hull in Figure 1). The tape covers and holds the !rst 2 inches against the hull; a remaining 4 inches of each strip are left to move as independent "aps. The e#ective waterline is just below the yellow tape, such that the foam "aps are slightly submerged. The "exible response of the "aps damps heave motions, helping keep the dome end-cap and antenna above the surface.
There is also a natural frequency for the tilting (pitch and roll changes) of any buoy. The octopus collar helps damp these motions too, such the buoy remains mostly upright in the water. Deviations from vertical are ignored in onboard data processing because the GPS velocity method is agnostic to buoy orientation. It is simply the lateral translation that matters for u; v. The pitch and roll do not a#ect this, so long as the antenna is close to the center of rotation (Thomson et al. (2018) provide a !rst-order correction for antennas above the axis of rotation, which is generally small if <1 m.). An IMU-based approach would be much more sensitive to pitch and roll changes, and corrections from the body reference frame to the earth reference frame would be required (Rainville et al. 2023).

### 4.3. Rotary test stand

Prior to testing in real ocean waves, the !delity of wave motion quanti!cation can be evaluated with a rotary test stand that simulates orbital wave motion of known amplitude and period. We built a simple version using

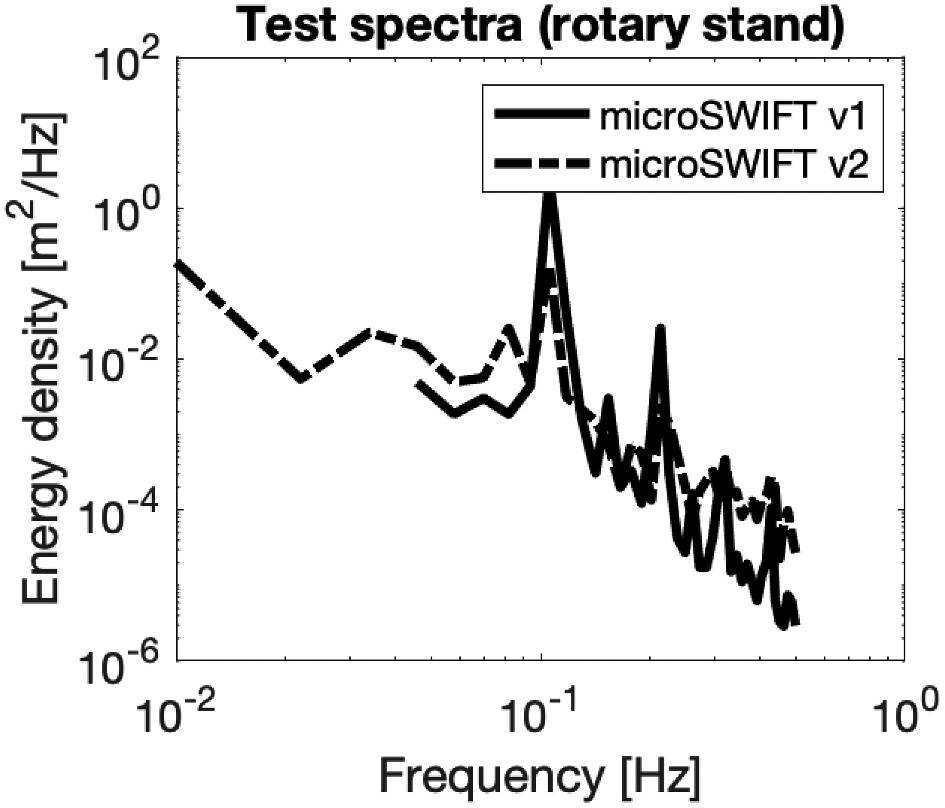
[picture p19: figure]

a DC motor, belt-drive, and bicycle mechanic stand. This was used to test both v1 and v2 buoys at amplitudes of 0.5 m (H à 1 m) and periods 4 and 10 seconds. For onboard GPS processing, testing indoors produced inferior results even when using a GPS repeater from the roof of the building. Another problem with the rotary test stand is the presence of harmonics in the spectral results, which are presumably from a mechanical instability in the test stand.
Figure 4 shows the results of testing on the rotary stand. Both the v1 and v2 buoys show a clear peak at the driven frequency f à 0:1 Hz, as well as a harmonic in the stand around f à 0:2 Hz. The background levels in Figure 4 are consistent with the static noise testing in Figure 2.

### 4.4. Air-drop tests

A series of air-drop tests have re!ned the approach to aerial deployment of the microSWIFTs. The initial tests were simply drops from static platforms less than 50 ft in height (i.e. the upper deck of research vessels and coastal piers) to con!rm the electronics and hull were robust. Testing then progressed to dropping from the open door of helicopters (approx. 100 ft height), with the addition of small nylon drogues (24 inch-diameter parachutes). Next, the buoys were packaged in cardboard tubes, with drogues stu#ed in the top, for deployment from the A-sized dropsonde tubes of Twin Otter and P-3 research aircraft. This was !rst tested Sept 2021 from a NOAA Twin Otter, then retested in May 2022 from the open-door of a sky-diving plane, then tested in July 2022 with the tube of a P-3 operated by the NRL (Navy Research Laboratory) VXS-1 squadron. Operational deployments from the NRL P-3 followed in Sept 2022 ahead of Hurricane Ian’s landfall on the Gulf coast of Florida. The survival rate from a total of 64 drops conducted to-date is 90%. Success is

Figure 3. Time series of heave response during free decay test
of 2-L buoy. | Figure 4. Energy spectra rotary test stand operating at approx- imate 10 second period (f ⇡ 101 Hz).

1
An octopus technically has six arms and two legs, so this name is not as inaccurate as it might at first seem..

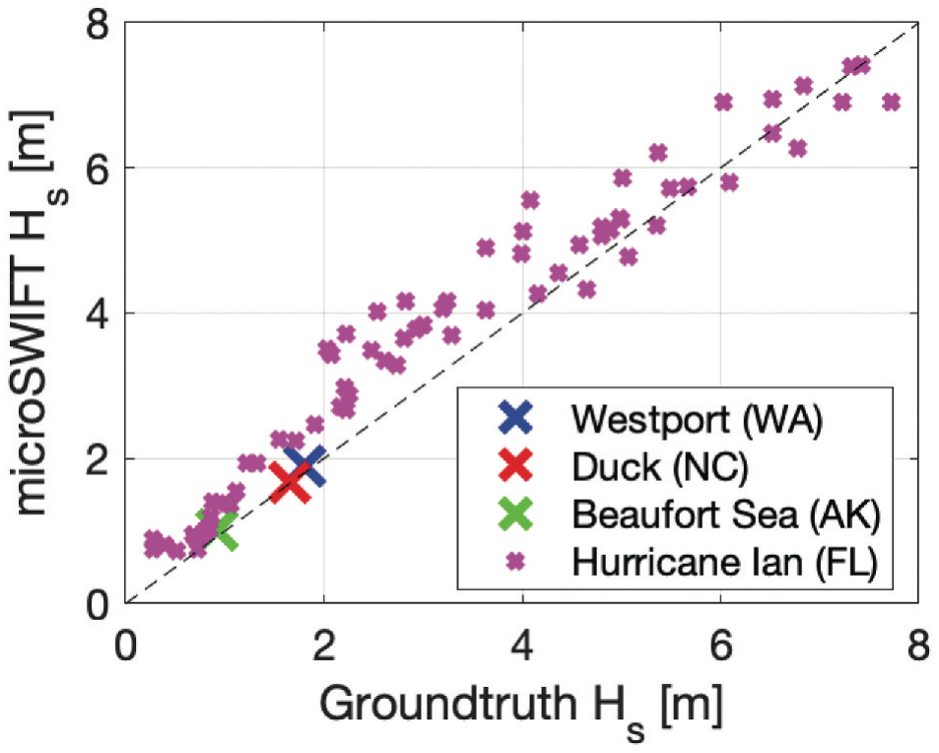
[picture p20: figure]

generally associated with lower airspeeds (100 130 knots) and altitudes (300 1000 feet). Testing is ongoing, especially at the higher air-speeds ( >200 knots) and altitudes (10; 000 ft) required for NOAA P-3 Hurricane Hunter missions.
The established rigging method is to encase the microSWIFT in a cardboard tube, which is split lengthwise and then bound around the microSWIFT with dissolving tape. The tape dissolves rapidly once the buoy hits the water, and the two halves of the cardboard separate to release the buoy to "oat freely. The bottom of the cardboard tube has several discs of cardboard that act as a crumple zone at the moment of impact with the water. The top of the cardboard tube has the aerial drogue stu#ed inside, and a small tail of webbing protruding. The webbing "utters and pulls the drogue from the tube once released from the aircraft. This provides an important delay in the drogue deployment, and thereby insures both safe separation from the aircraft and reduced load on the drogue. The drogue provides only a modest reduction in the fall velocity of the buoy; it is not truly a parachute, but it does help the buoy maintain orientation in air. The drogue is not directly connected to the buoy, rather it is connect to the cardboard using a webbing bridle that threads through each half and below the buoy. Thus, it also washes free of the buoy upon entering the water.

### 5. Buoy deployments

A series of !eld deployments, summarized in Table 3, have validated and improved the microSWIFTs. These deployments span routine coastal measurements to extremes (Arctic, hurricanes). Figure 5 compares the microSWIFT signi!cant wave heights Hs during each test with some form of ground truth or other independent estimate of Hs. The 2021 tests were all short in duration and limited in Hs range, compared with the 2022 deployment during Hurricane Ian. The Ian deployments, however, su#er from a lack of truly collocated ground truth measurements. The scatter in the collocated testing from 2021 is within the ⌃0:1 m error in Hs expected from the static noise testing. The scatter in the Ian 2022 dataset is larger, most likely because the Spotter buoy used for groundtruth was 50–100 km away from the microSWIFT.
Spectral comparisons and details for each test are in the subsections that follow. The short-duration tests from 2021 are presented together in Figure 6 and include results from onboard processing of the IMU data. This was discontinued in later tests, because su%cient !ltering of the raw IMU data was not achieved onboard (because of limited computing power). The early tests do not include directional moments (a1; b1; a2; b2), because of a software bug invalidated most the results. These issues were addressed prior to the Hurricane Ian deployments, and thus we focus on the Ian results as a more comprehensive evaluation of the microSWIFTs (including the directional moments).

### 5.1. Westport (Washington State, USA)

Brief test deployments were conducted o#shore of Westport and Grays Harbor, Washington State (USA), where a Datawell waverider is maintained as CDIP station 036. There are strong tidal currents at the mouth of Grays Harbor, and adjusting for the Doppler shift between the moored Waverider and the drifting microSWIFTs is important. Testing occurred for a few hours in July 2021 with several

Table 3. microSWIFT deployments.
Project | Location | Dates | Method | Groundtruth | Hs range
Westport testing | WA coast | July 2021 | Vessel | Waverider | 2 3 m
DUNEX | Duck FRF | Oct 2021 | Air (helicopter) | Waverider | 1 2 m
Arctic coastal ice | Beaufort Sea | Sept 2021 | Air (Twin Otter) | none | 1 2 m
NHCI | Gulf of Mexico | Sept 2022 | Air (P3) | Spotter | 1 8 m

Figure 5. Comparison of significant wave heights during field deployments.

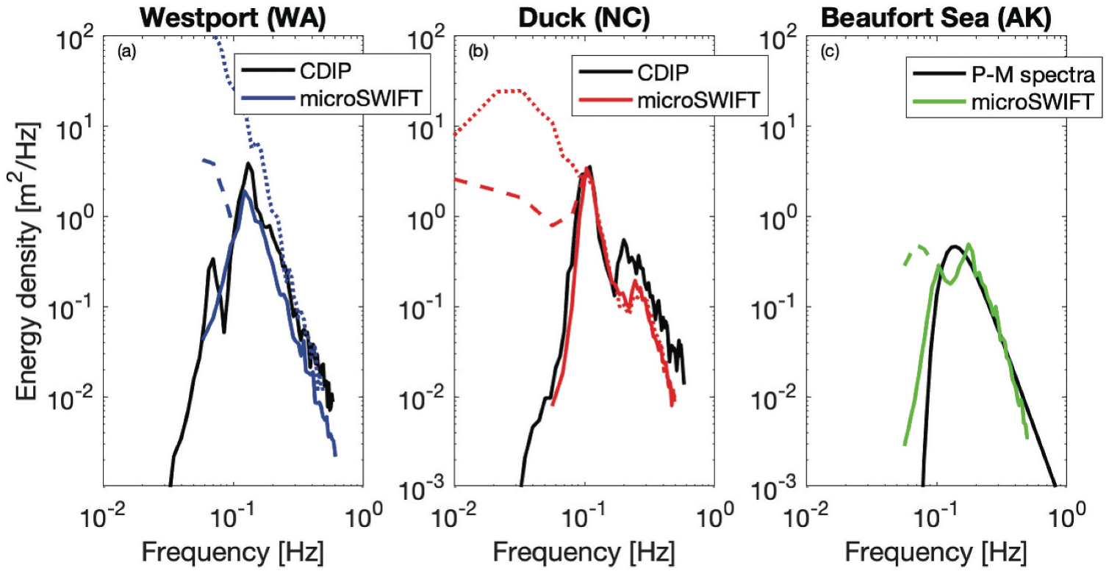
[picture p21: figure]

v1 microSWIFTs. The microSWIFTs were allow to drift past the moored waverider and were reset once to stay within 500 m of the waverider. Figure 6a shows the spectral agreement between the Waverider and the microSWIFTs. The GPS results are in good agreement, though the !lter is clearly essential to that agreement. The IMU results agree at the highest frequencies, but deviate dramatically at the middle and low frequencies. The aforementioned integration error in the IMU spectral results is severe, such that the RC !lter is unable to recover a reasonable result.

### 5.2. Duck FRF (North Carolina, USA)

There were extensive v1-1 L microSWIFT deployments during the 2021 DUNEX experiment at the US Army Corps of Engineers Field Research Facility in Duck, NC (USA). The data and IMU post-processing are described in detail in Rainville et al. (2023). These deployments were focused on nearshore dynamics, but buoys drifted o#shore on a few occasions that provide opportunistic validation of wave spectra from the onboard GPS processing. Figure 6b shows the spectral comparison of microSWIFT drifting past the Datawell Waverider CDIP 192 on October 26 2021. The GPS results are in good agreement, though again the !lter is clearly essential to that agreement. The microSWIFT was 59 km from the waverider, and there are some di#erences in the secondary wind-wave peak around f à 0:5 Hz that are likely related to small scale wind variations and sea breeze along the coast. As in the previous test, the IMU results have severe errors at low frequencies that overwhelm the RC !lters.

### 5.3. Beaufort sea (Alaska, USA)

Ongoing aerial deployments in the seasonally icecovered Beaufort Sea intend to quantify the dissipation of energy by shorefast ice (e.g. Thomson et al. 2021) and calibrate observations from Distributed Acoustic Sensing (DAS) using a sea"oor !ber optic cable (Baker and Abbott 2022; Smith et al. 2023). Deployments to-date have focused on the early and late portions of the open-water season, speci!cally in the months of September 2021, November 2021, , and June 2022. Figure 6c shows spectra from Sept 2021. No other buoys or wave measurments were available as groundtruth, and thus a parametric Pierson-Moskowitz spectra based on observed 10 m/s winds is used for comparison.

### 5.4. Hurricane Ian

Hurricane Ian was a major hurricane (category IV) that made landfall in Florida in Sept 2022. As part of the NOPP Hurricane Coastal Impacts (NHCI) Program, an array of wave buoys was deployed ahead of the storm using a P-3 aircraft operated by the Navy’s VXS-1 Scienti!c Development Squadron. These have been used to understand the saturation of wave slopes under extreme winds (Davis et al. 2023), while also providing an opportunity for full scale validation of the microSWIFTs. These were open-door deployments ahead of the storm. Future deployments will also use the dropsonde tube of NOAA P-3 aircraft "ying inside the storm, which can more accurately target the track of the storm in real-time. (This 2 L size microSWIFT was recently certifed for deployment from the NOAA P-3.)

Figure 6. Spectra from early testing of microSwifts (v1). The solid colored lines are the GPS-based onboard processing. The dashed lines are the GPS-based result without the high-pass filter. The dotted lines are the IMU-based onboard processing, which were abandoned in the later testing because of insufficient filtering.

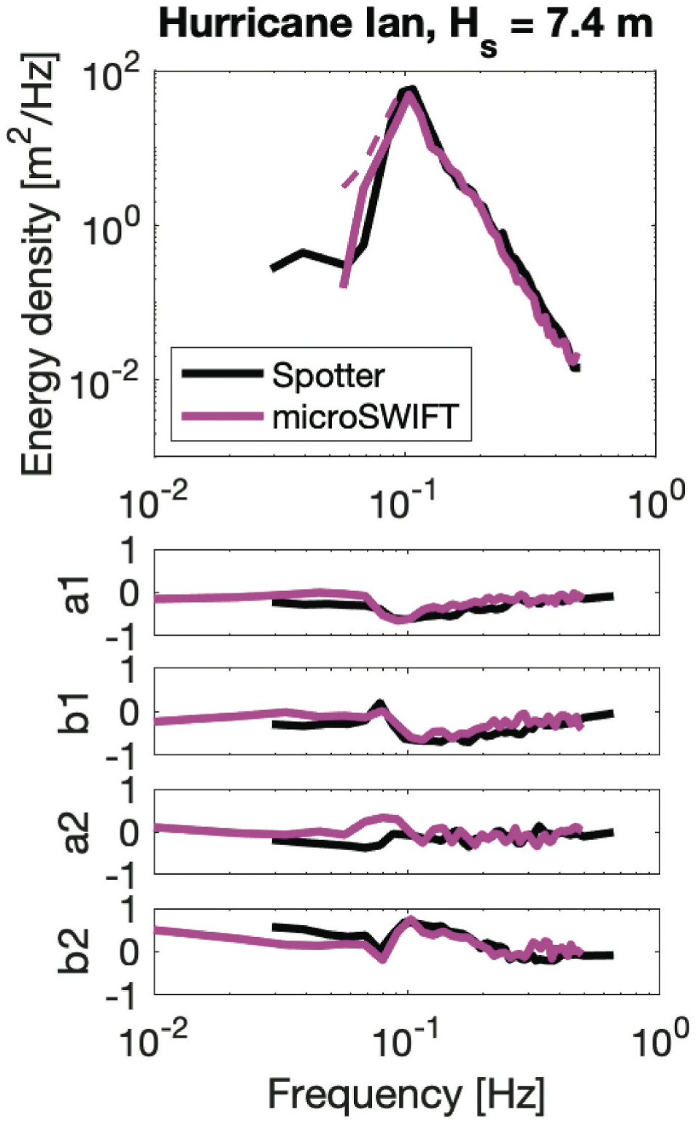
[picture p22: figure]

Spectral comparisons between a microSWIFT and a Spotter are shown in Figures 7 to 9. Each !gure has the scalar energy (with and without !ltering), along with the normalized directional moments. Figure 7 shows the maximum conditions (Hs à 7:4
m) as hurricane passed through the buoy array. Figure 8 shows the energetic conditions (Hs à 4:3
m) immediately following the hurricane. Figure 9 shows the calmer conditions (Hs à 2:7 m) one day after the hurricane. The agreement between the buoys is strong across all conditions and for all spectral quantities. Quantities derived from these spectra also are in agreement, including full 2-D directional spectra (not shown) that can be reconstructed from the moments a1; b1; a2; b2. The slight di#erences between buoys at low frequencies has a negligible e#ect on derived quantities, because the energy levels at those frequencies are so low. These three spectral comparisons are representative of the larger dataset, which includes 68 total observations (i.e. the hourly Hs results in Figure 5).

### 6. Discussion

Though the beta version of the microSWIFT was based on GPS velocity data for wave estimation, the initial design for production versions of the microSWIFTs assumed that IMU data would become the preferred source for wave estimation. This assumption was based on the plethora of low-cost and low-power IMUs now available for consumer electronics. As shown by Rainville et al. (2023), the IMU data collected by microSWIFTs is certainly valuable for resolving the kinematics of individual waves, as well as for detecting the onset and strength of breaking waves. However, such usage requires careful post-processing, with band-pass

Figure 7. Spectral results, including directional moments, from a v1 (2L) microSWIFT near a Spotter buoy during Hurricane Ian (Sept 2022). The dashed line is the spectra without a high-pass filter; the solid line includes a high-pass filter. The buoys were 87 km a part during this observation. Spotter data courtesy of Sofar Ocean, Inc.

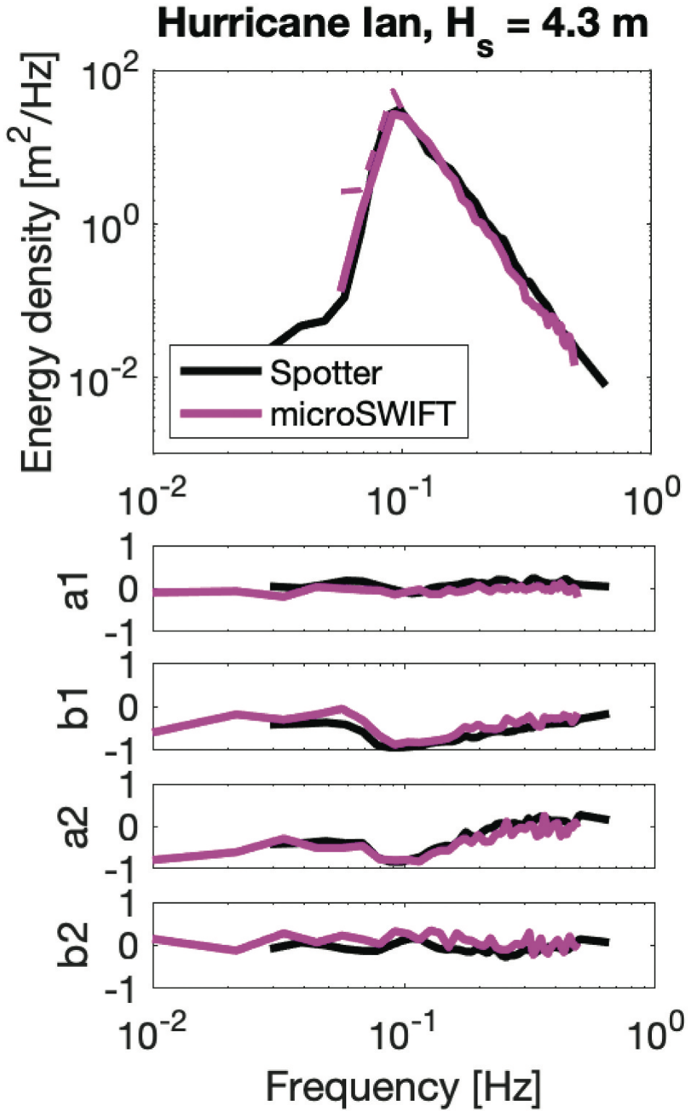
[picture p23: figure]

!lters that are tuned to wave motion and sensor fusion algorithms that include noise characteristics of the linear accelerometers, gyroscopes, and magnetometers. The v1 microSWIFTs included both IMU-based and GPS-based onboard processing, with a "ag in the Iridium SBD telemetry packet to identify the data source for each spectral result. As shown in Figure 6, the onboarding processing of IMU data produced results with severe bias at low frequencies.
Use of the IMU data required assuming the vertical axis of the body reference frame was nearly aligned with the vertical axis of the earth reference frame (i.e. a strapped-down accelerometer). This assumption fails in extreme sea states (e.g. hurricanes) and causes large errors in estimation of directional moments a1; b1; a2; b2 from Euler angles (i.e. pitch and roll) in any sea state. Furthermore, the magnetometer readings, which are used to determine heading, require calibration within the buoy housing to remove the e#ects of additional magnetic !elds from batteries and ferrous metals. Based on the di%culties in calibration and tuning of low-cost IMUs, along with the relatively poor agreement between the IMU onboard processing and the groundtruth measurements, the GPS method is the only onboard processing carried forward into v2.
Even the onboard processing of GPS data required !ltering to remove low-frequency noise. This is a persistent problem when using motion data to estimate position. Use of GPS velocities causes a characteristic f 2 shape of the noise "oor. Use of acceleration would cause f 4. Either may by appreciable, relative to the true wave signal, at lower frequencies.
The other surprising aspect of microSWIFT development has been the challenge of working with non-spherical hull shapes. The cylindrical shape used throughout is required for aerial deployments from the drop sonde tube of research aircraft operating at high altitudes with pressurized cabins (i.e. no open-door deployment option). This cylindrical shape makes it di%cult to achieve a balance of buoyancy, which is necessary to keep the GPS and Iridium antenna clear, and stability, which is necessary to avoid resonant hydrodynamic response of

Figure 8. Spectral results, including directional moments, from a v1 (2L) microSWIFT near a Spotter buoy immediately following Hurricane Ian (Sept 2022). The dashed line is the spectra without a high-pass filter; the solid line includes a high-pass filter. The buoys were 63 km a part during this observation. Spotter data courtesy of Sofar Ocean, Inc.

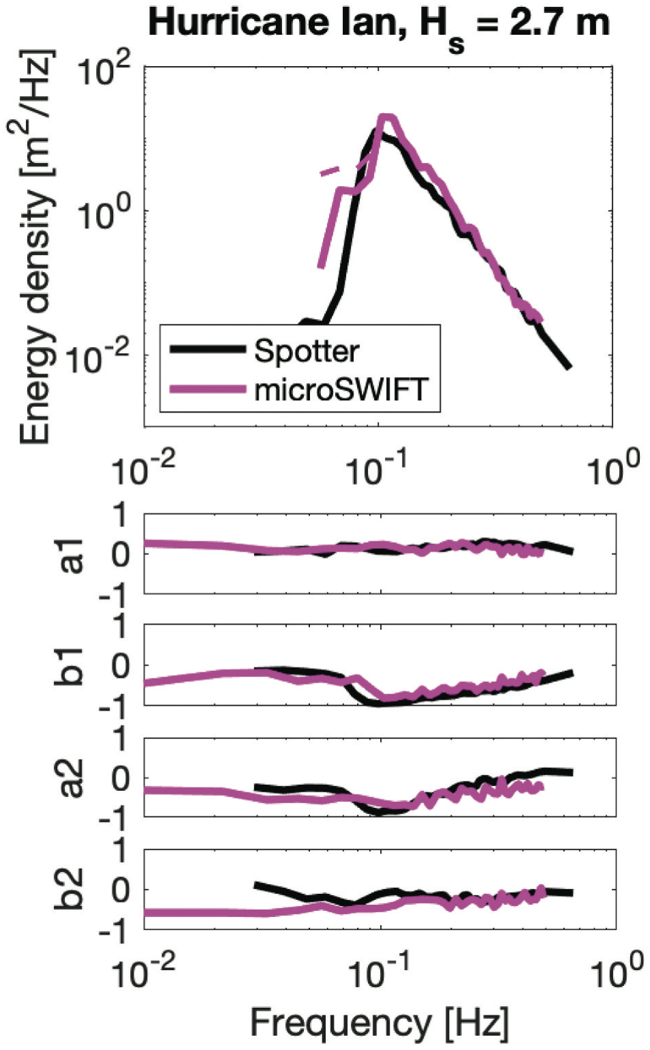
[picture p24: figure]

the buoy. The primary solution has been to add a thin foam octopus collar around the waterline of the microSWIFT hull, which has "exible "aps that fold along the hull when packaged in a cardboard deployment tube. The foam unfolds in the water and provides both additional buoyancy and partial damping of buoy resonance. The secondary solution has been to use GPS velocities as the wave data source because these velocities are agnostic to buoy orientation and are natively in the earth reference frame (not the buoy reference frame). Following on the favorable comparisons between microSWIFTs and various groundtruth measurements across the !eld tests, we note that inter-calibration of wave measurements remains a di%cult task. As shown by Collins et al. (2024), direct comparisons are often limited by operational constraints, including: mooring dynamics, spectral resolution, buoy endurance, di#erences in !ltering, and di#erences in parameter de!nitions. Beyond the practical constraints, there is also the problem of statistical estimates of random waves from

!nite records. The convention for wave parameter estimation every 30 or 60 minutes is driven by a requirement for stationarity in the sea state. A 30-minute record might contain over 1,000 realizations for the shorter waves, but only a few hundred realizations for the longer waves. This is enough for robust statistics at all scales since errors in the bulk parameters will reduce with the number of realizations N by a factor 1ÅÅ
N

p , but it
can never give the true value that an in!nite record will provide. Even small di#erences in either location or record length will cause non-zero di#erences in bulk parameters. For the case of buoys drifting independently for several days, such as the Hurricane Ian deployment, the conditions for comparison become far less than ideal.

### 7. Conclusions

The development of miniature, expendable versions of SWIFT buoy has included iterations on processors, housing, and sensors. Each have been

Figure 9. Spectral results, including directional moments, from a v1 (2L) microSWIFT near a Spotter buoy one day after Hurricane Ian (Sept 2022). The dashed line is the spectra without a high-pass filter; the solid line includes a high-pass filter. The buoys were 66 km a part during this observation. Spotter data courtesy of Sofar Ocean, Inc.

tested to verify sensor noise, hydrodynamic response, spectral !delity, and aerial survival. Field deployments have spanned a range of environments and wave conditions, including hurricanes and Arctic seas. The microSWIFT buoys are speci!cally designed for the dropsonde tube of research aircraft, and this opens possibilities for numerous future applications.

### 8. Data and code availability

Telemetry data from all microSWIFTs and SWIFTs are available via public server (see Data tab at www.apl.washington.edu/SWIFT). All associated codes are in repos at https://github.com/SASlabgroup. (https://github.com/SASlabgroup) Speci!c projects and publications using microSWIFT data have additional archives, such as Dryad https://doi.org/10.5061/dryad. g4f4qrfvb (https://doi.org/10.5061/dryad.g4f4qrfvb) and https://doi.org/10.5061/dryad. hx3#bgk0. (https://doi.org/10.5061/dryad.hx3ffbgk0)

Acknowledgments

We thank Kapowsin Skydiving, NRL VXS-1, NOAA AOC, Pollux Aviation, and OBX helicopters for support in aerial testing. We thank Dakota Mascarenas, Lily Nguyen, Melissa Moulton, Morteza Derakhti, Emma Nuss, Christine Baker for help with test deployments. We thank Jean Rabault and Gaute Hope for numerous discussions about microprocessors and code development.

Disclosure statement

No potential con"ict of interest was reported by the author(s).

Funding

Development and testing of microSWIFT buoys has been funded by the US O%ce of Naval Research (DURIP, N00014-20-1-2456; SIZRS, N00014-21-1-2868), the US Naval Facilities Engineering Command (N00024-18-F-8702), the US National Science Foundation (CODAS, OPP-2215134), and the US Coastal Research Program (W912HZ1920045).

ORCID

Jim Thomson | http://orcid.org/0000-0002-8929-0088
Jacob Davis | http://orcid.org/0000-0001-8623-2141
Edwin James Rainville | http://orcid.org/0000-0001-8781-
5242

References

Baker, Michael G., and Robert E. Abbott. 2022. “Rapid Refreezing of a Marginal Ice Zone Across a Sea"oor Distributed Acoustic Sensor.” Geophysical Research Letters

49 (24). https://doi.org/10.1029/2022GL099880. n/a (n/a): e2022GL099880. E2022GL099880 2022GL099880. Collins, C.O., P. Dickhudt, J. Thomson, T. de Paolo, M. Otero, S. Merri!eld, E. Terril, M. Schonau, L. Braasch, T. Paluszkiewicz, and L. Centurioni. “Performance of Moored GPS Wave Buoys.” Journal of Atmospheric and Oceanic Technology.
Davis, Jacob, Jim Thomson, Isabel A. Houghton, James D. Doyle3, Will Komaromi, Chris W. Fairall, Elizabeth J. Thompson, and J. R. Moskaitis. 2023. “Saturation of Ocean Surface Wave Slopes Observed During Hurricanes.” Geophysical Research Letters 50 (16). https://doi.org/10.1029/2023GL104139. (https://doi.org/10.1029/2023GL104139)
Feddersen, F., A. Amador, K. Pick, A. Vizuet, K. Quinn, E. Wol!nger, J. H. MacMahan, et al. 2024. “The Wavedrifter: A Low-Cost IMU-Based Lagrangian Drifter to Measure Surface Gravity Waves from Quasi-Linear to Overturning and the Transition to Turbulence.“ Coastal Engineering Journal 1–14. https://doi.org/10.1080/21664250.2023. 2238949. (https://doi.org/10.1080/21664250.2023.2238949)
Herbers, T. H. C., P. F. Jessen, T. T. Janssen, D. B. Colbert, and J. H. MacMahan. 2012. “Observing Ocean Surface Waves with GPS Tracked Buoys.” Journal of Atmospheric and Oceanic Technology 29 (7): 944–959. https://doi.org/10.1175/JTECH-D-11-00128.1. (https://doi.org/10.1175/JTECH-D-11-00128.1)
Kuik, A. J., G. P. Van Vledder, and L. H. Holthuijsen. 1988. “A Method for the Routine Analyis of Pitch-And-Roll Buoy Wave Data.” Journal of Physical Oceanography 18 (7): 1020–1034. https://doi.org/10.1175/1520-0485 (1988)018<1020:AMFTRA>2.0.CO;2. (https://doi.org/10.1175/1520-0485(1988)018%3C1020:AMFTRA%3E2.0.CO;2)
Perfect, B., Jim Thomson, Jim Riley, and Endicott Fay. 2015. Washington State Ferries Rich Passage Wake Study. Technical Report. Washington State Department of Transportation. Rabault, Jean, Takehiko Nose, Gaute Hope, Malte Müller, Øyvind Breivik, Joey Voermans, Lars Robert Hole, et al.
2022. | “OpenMetbuoy-v2021: | An | Easy-To-Build,
A#ordable, Customizable, Open-Source Instrument for Oceanographic Measurements of Drift and Waves in Sea Ice and the Open Ocean.” Geosciences 12 (3): 3. https://www.mdpi.com/2076-3263/12/3/110 .
Rabault, Jean, Graig Sutherland, Olav Gundersen, Atle Jensen, Aleksey Marchenko, and Øyvind Breivik. 2020. “An Open Source, Versatile, A#ordable Waves in Ice Instrument for Scienti!c Measurements in the Polar Regions.” Cold Regions Science and Technology 170:102955. https://doi.org/10.1016/j.coldregions.2019. 102955. (https://doi.org/10.1016/j.coldregions.2019.102955)
Raghukumar, Kaustubha, Grace Chang, Frank Spada, Craig Jones, Tim Janssen, and Andrew Gans. 2019. “Performance Characteristics of “Spotter,” a Newly Developed Real-Time Wave Measurement Buoy.” Journal of Atmospheric and Oceanic Technology 36 (6): 1127–1141. https://doi.org/10.1175/JTECH-D-18-0151.1. (https://doi.org/10.1175/JTECH-D-18-0151.1)
Rainville, E. J., J. Thomson, M. Moulton, and M. Derakhti. 2023. “Measurements of Nearshore Waves Through Coherent Arrays of Free-Drifting Wave Buoys.” Earth System Science Data. https://doi.org/10.5194/essd-2023-64.
Smith, M. M., J. Thomson, M. G. Baker, R. Abbott, and J. Davis. 2023. “Observations of Ocean Surface Wave Attenuation in Sea Ice Using Sea"oor Cables.” Geophysical Research Letters in revision. https://doi.org/10.22541/essoar.168889938.88368062/v1. (https://doi.org/10.22541/essoar.168889938.88368062/v1)

Thomson, Jim. 2012. “Wave Breaking Dissipation Observed with SWIFT Drifters.” Journal of Atmospheric and Oceanic Technology 29 (12): 1866–1882. https://doi.org/10.1175/JTECH-D-12-00018.1. (https://doi.org/10.1175/JTECH-D-12-00018.1)
Thomson, Jim, James B. Girton, Rajesh Jha, and Andrew Trapani. 2018. “Measurements of Directional Wave Spectra and Wind Stress from a Wave Glider Autonomous Surface Vehicle.” Journal of Atmospheric and Oceanic Technology 35 (2): 347–363. https://doi.org/10.1175/JTECH-D-17-0091.1. (https://doi.org/10.1175/JTECH-D-17-0091.1)
Thomson, Jim, Lucia Hošeková, Michael H. Meylan, Alison L Kohout, and Nirnimesh Kumar. 2021. “Spurious Rollover of

Wave Attenuation Rates in Sea Ice Caused by Noise in Field Measurements.” Journal of Geophysical Research: Oceans 126 (3): e2020JC016606. n/a (n/a)E2020JC016606 2020JC016606. https://agupubs.onlinelibrary.wiley.com/doi/abs/10.1029/2020JC016606 (https://agupubs.onlinelibrary.wiley.com/doi/abs/10.1029/2020JC016606) .
Thomson, Jim, Joe Talbert, Alex de Klerk, Adam Brown, Mike Schwendeman, Jarett Goldsmith, Julie Thomas, Corey Olfe, Grant Cameron, and Christian Meinig. 2015. “Biofouling E#ects on the Response of a Wave Measurement Buoy in Deep Water.” Journal of Atmospheric and Oceanic Technology 32 (6): 1281–1286. https://doi.org/10.1175/JTECH-D-15-0029.1. (https://doi.org/10.1175/JTECH-D-15-0029.1)

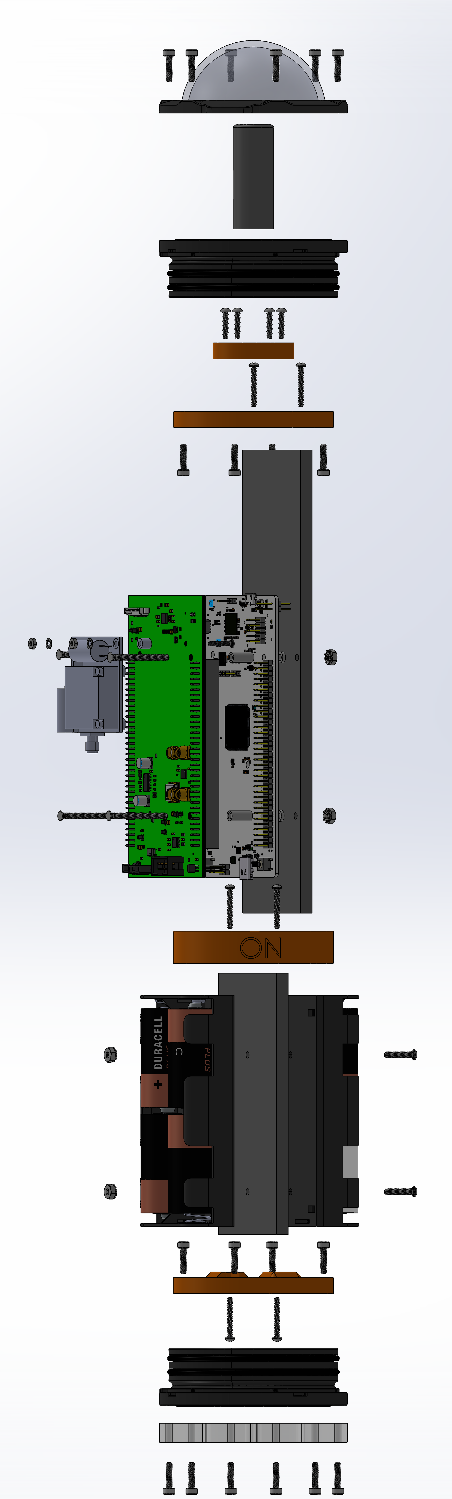
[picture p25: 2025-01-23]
hardware/ExplodedView.PNG

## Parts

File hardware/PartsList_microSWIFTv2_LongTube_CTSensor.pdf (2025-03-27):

Parts List | microSWIFT v2, Long Tube w/ CT | Updated 2/9/24 A.dK

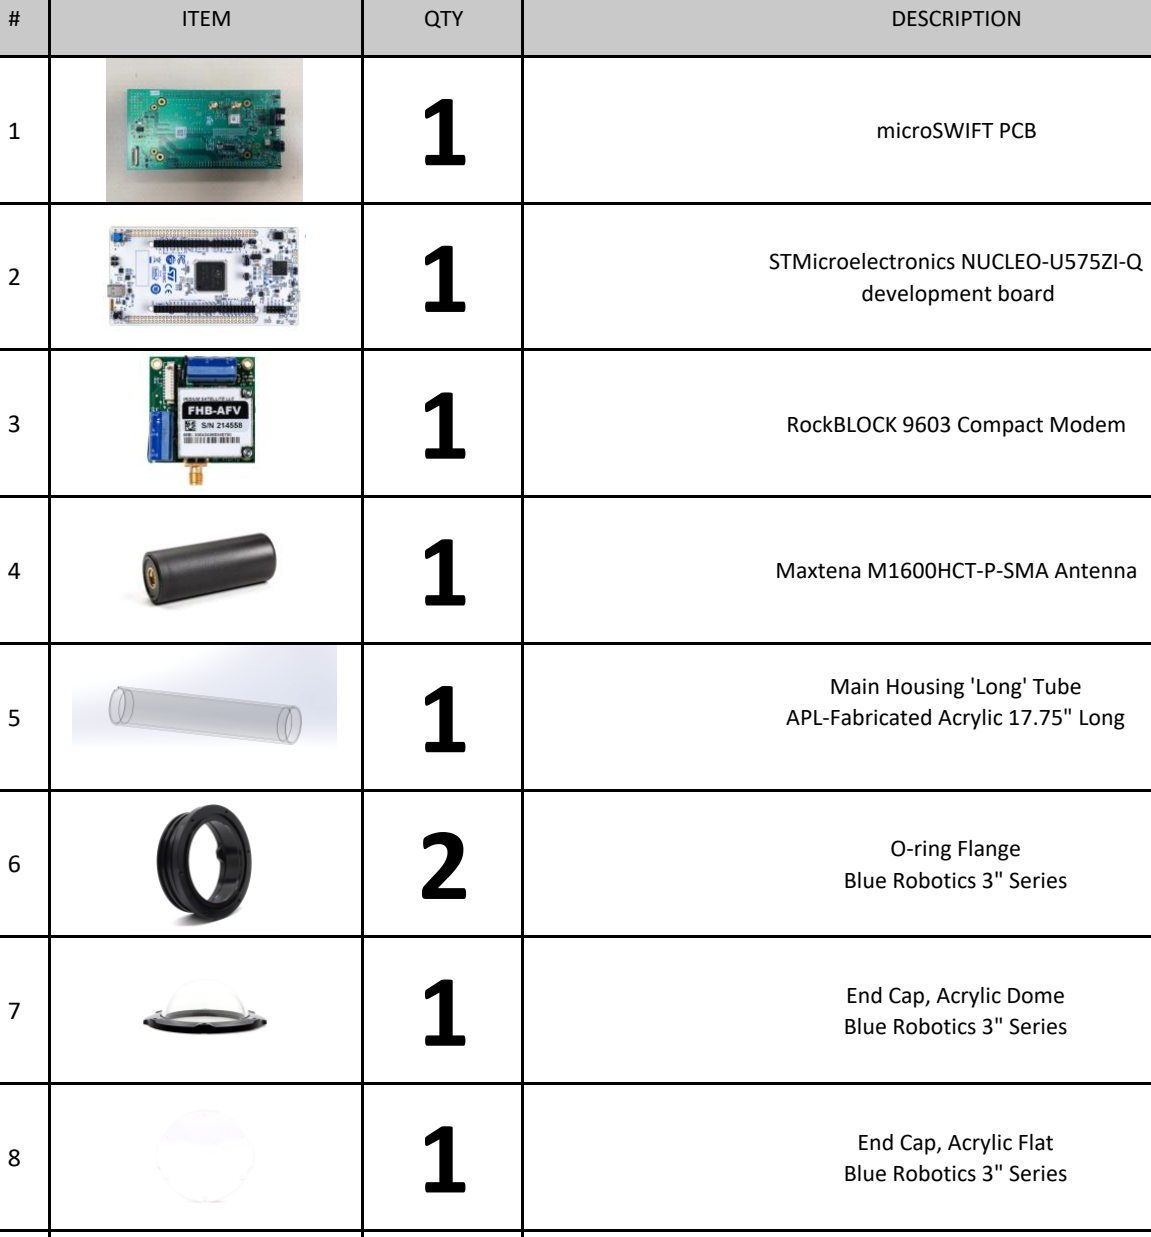
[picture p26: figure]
ITEM; QTY; DESCRIPTION; microSWIFT PCB; STMicroelectronics NUCLEO-U575ZI-Q development board; RockBLOCK 9603 Compact Modem; Maxtena M1600HCT-P-SMA Antenna

5 | | 1 | Main Housing 'Long' Tube APL-Fabricated Acrylic 17.75" Long
6 | | 2 | O-ring Flange Blue Robotics 3" Series
7 | | 1 | End Cap, Acrylic Dome Blue Robotics 3" Series
8 | | 1 | End Cap, Acrylic Flat Blue Robotics 3" Series
9 | | 4 | O-ring, Radial Seal, 3" Series -150 Buna-N 70A
10 | | 2 | O-ring, Face Seal, 3" Series -148 Buna-N 70A

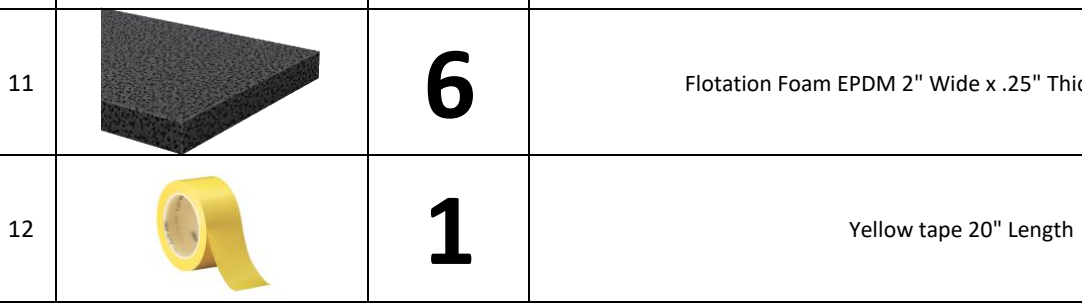
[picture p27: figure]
Yellow tape 20" Length

11 | | 6 | Flotation Foam EPDM 2" Wide x .25" Thickness x 6" Long

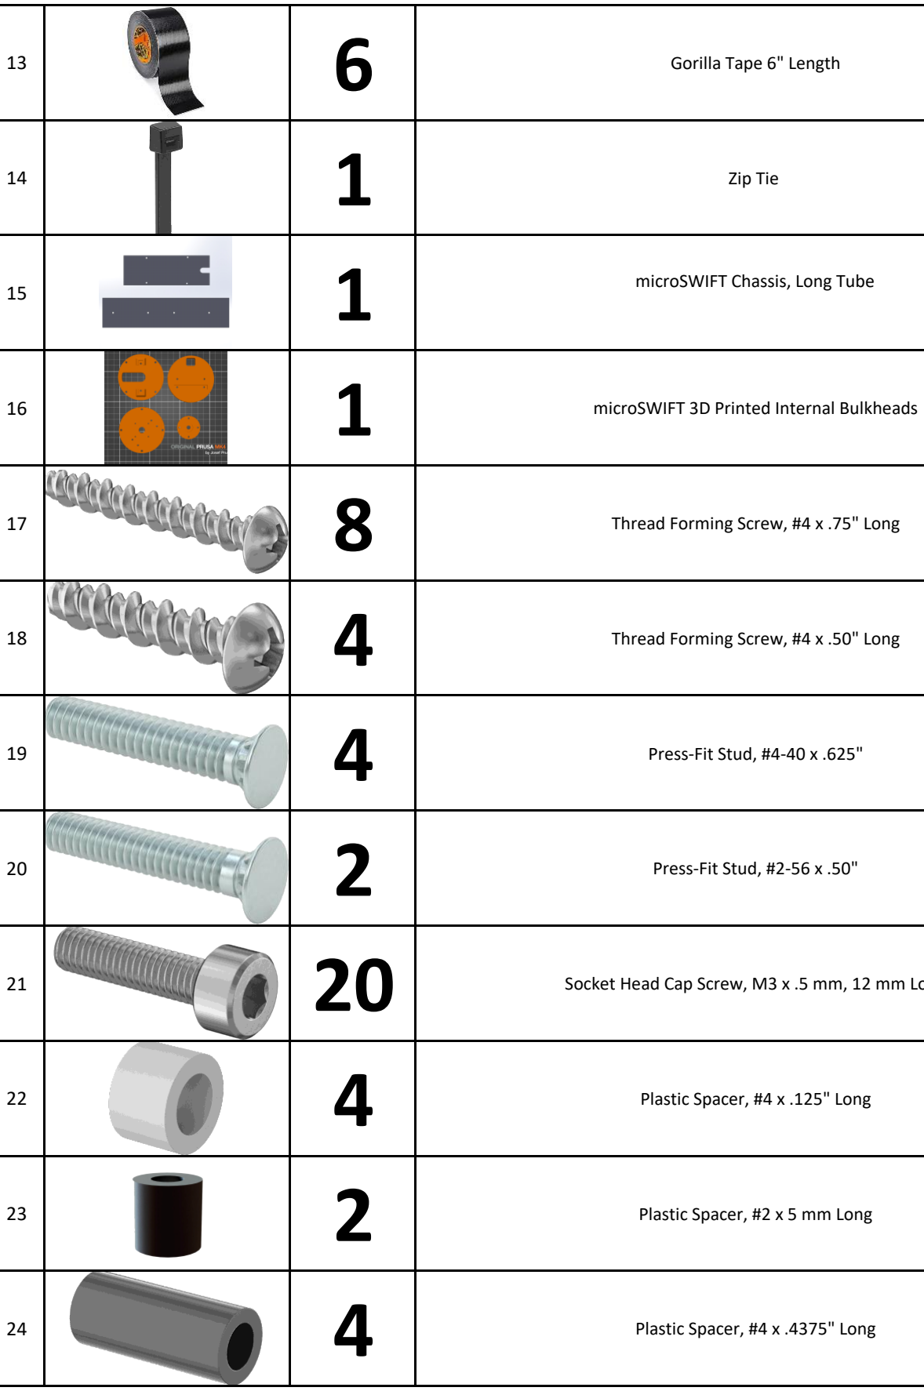
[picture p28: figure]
Gorilla Tape 6" Length; Zip Tie; microSWIFT Chassis, Long Tube; microSWIFT 3D Printed Internal Bulkheads; Press-Fit Stud, #4-40 x .625"; Press-Fit Stud, #2-56 x .50"; Plastic Spacer, #4 x .125" Long; Plastic Spacer, #2 x 5 mm Long; Plastic Spacer, #4 x .4375" Long

17 | 8 | Thread Forming Screw, #4 x .75" Long
18 | 4 | Thread Forming Screw, #4 x .50" Long
21 | 20 | Socket Head Cap Screw, M3 x .5 mm, 12 mm Long

25 | 4 | Socket Head Cap Screw, #4-40 x 1.25"

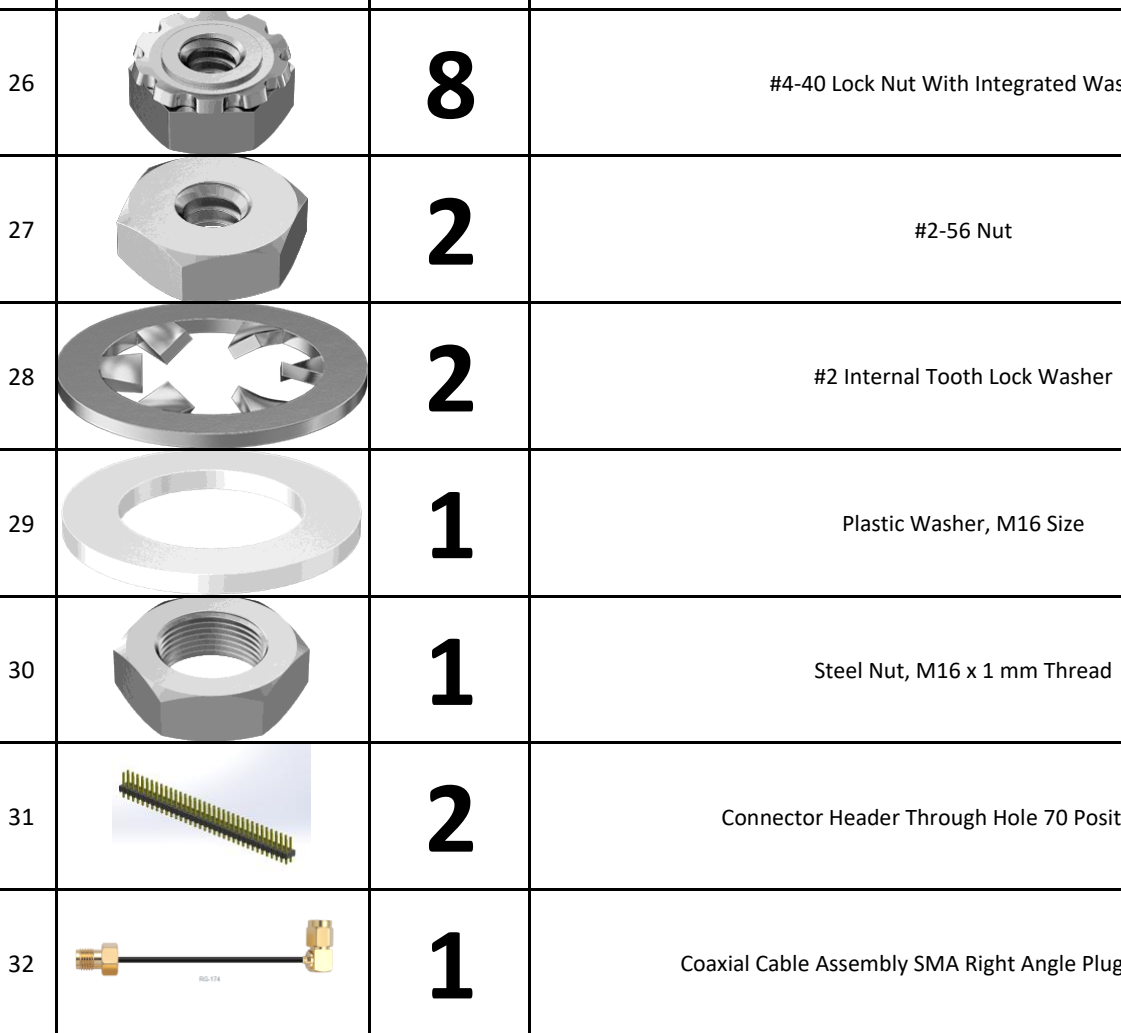
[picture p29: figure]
#2-56 Nut; #2 Internal Tooth Lock Washer; Plastic Washer, M16 Size; Steel Nut, M16 x 1 mm Thread

26 | 8 | #4-40 Lock Nut With Integrated Washer
31 | 2 | Connector Header Through Hole 70 Position 2x35
32 | 1 | Coaxial Cable Assembly SMA Right Angle Plug to SMA Jack

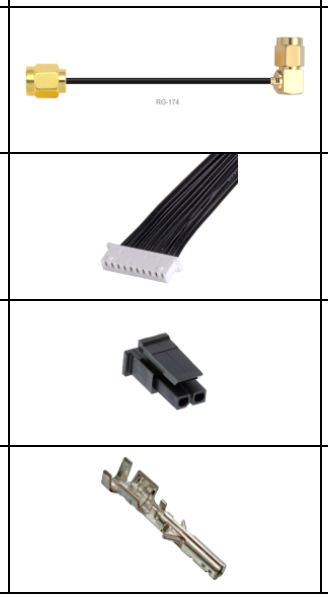
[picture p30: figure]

33 | 1 | Coaxial Cable Assembly SMA Right Angle Plug to SMA Plug
34 | 1 | Cable Assembly 10 Position Molex Picoblade Socket to Socket, 50 mm Long
35 | 1 | Connector Housing, Molex Micro-Fit 3.0 2 Position
36 | 2 | Connector Socket Contacts, Molex Micro-Fit 3.0

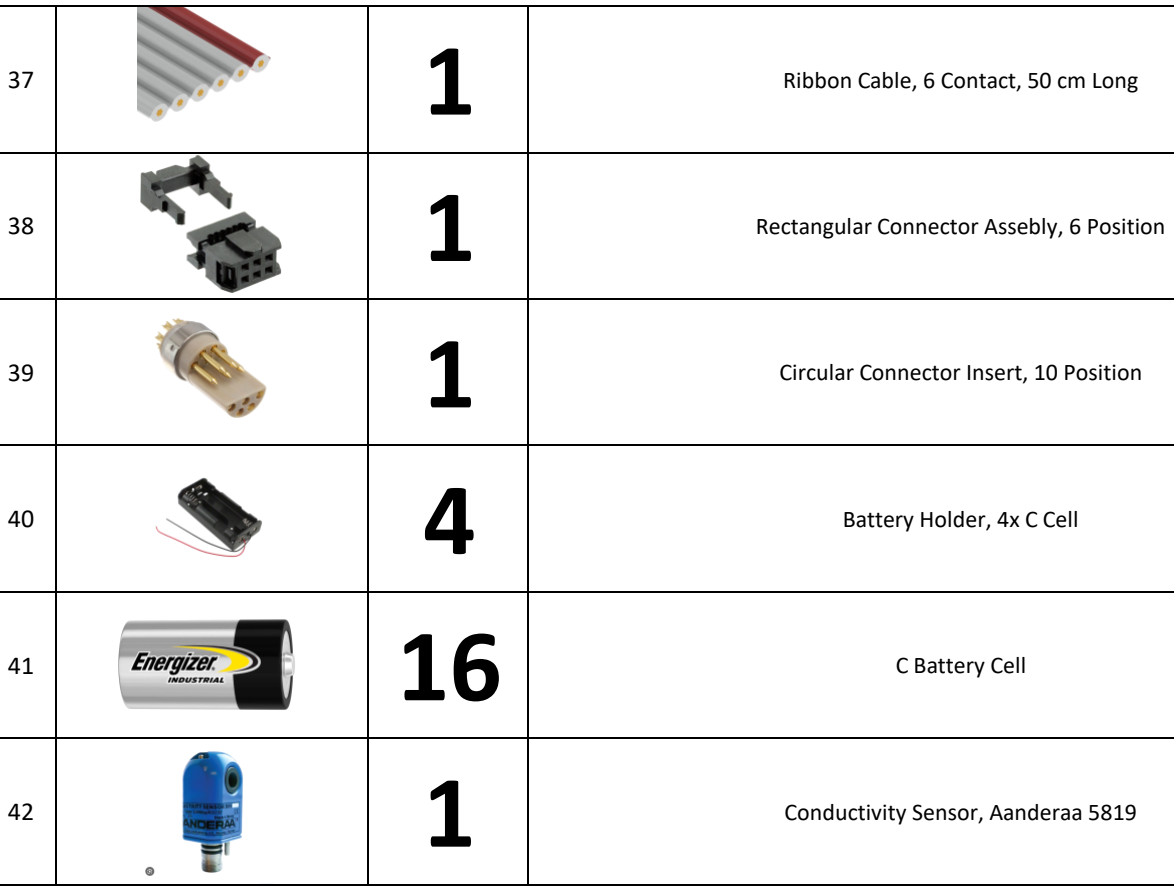
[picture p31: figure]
Rectangular Connector Assebly, 6 Position; Circular Connector Insert, 10 Position; Battery Holder, 4x C Cell; C Battery Cell; Conductivity Sensor, Aanderaa 5819

37 | 1 | Ribbon Cable, 6 Contact, 50 cm Long

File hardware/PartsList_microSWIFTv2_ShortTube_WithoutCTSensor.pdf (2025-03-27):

Parts List | microSWIFT v2, Short Tube, No CT | Updated 2/9/24 A.dK

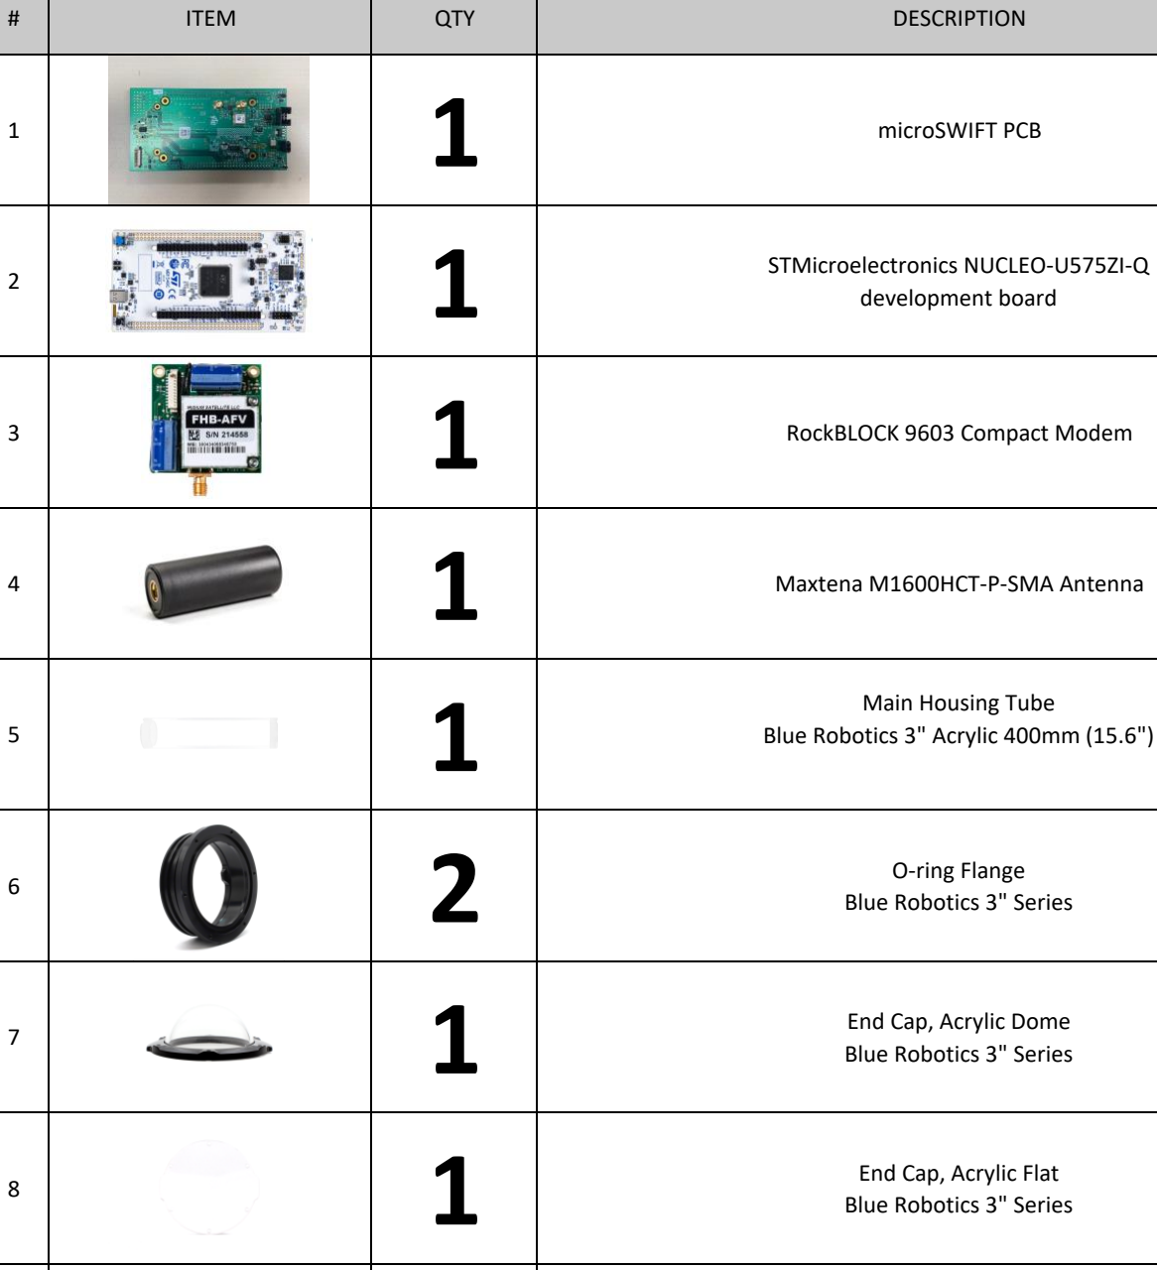
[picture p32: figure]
ITEM; QTY; DESCRIPTION; microSWIFT PCB; STMicroelectronics NUCLEO-U575ZI-Q development board; RockBLOCK 9603 Compact Modem; Maxtena M1600HCT-P-SMA Antenna

5 | | 1 | Main Housing Tube Blue Robotics 3" Acrylic 400mm (15.6")
6 | | 2 | O-ring Flange Blue Robotics 3" Series
7 | | 1 | End Cap, Acrylic Dome Blue Robotics 3" Series
8 | | 1 | End Cap, Acrylic Flat Blue Robotics 3" Series
9 | | 4 | O-ring, Radial Seal, 3" Series -150 Buna-N 70A
10 | | 2 | O-ring, Face Seal, 3" Series -148 Buna-N 70A
11 | | 1 | Lead Ballast 350 g

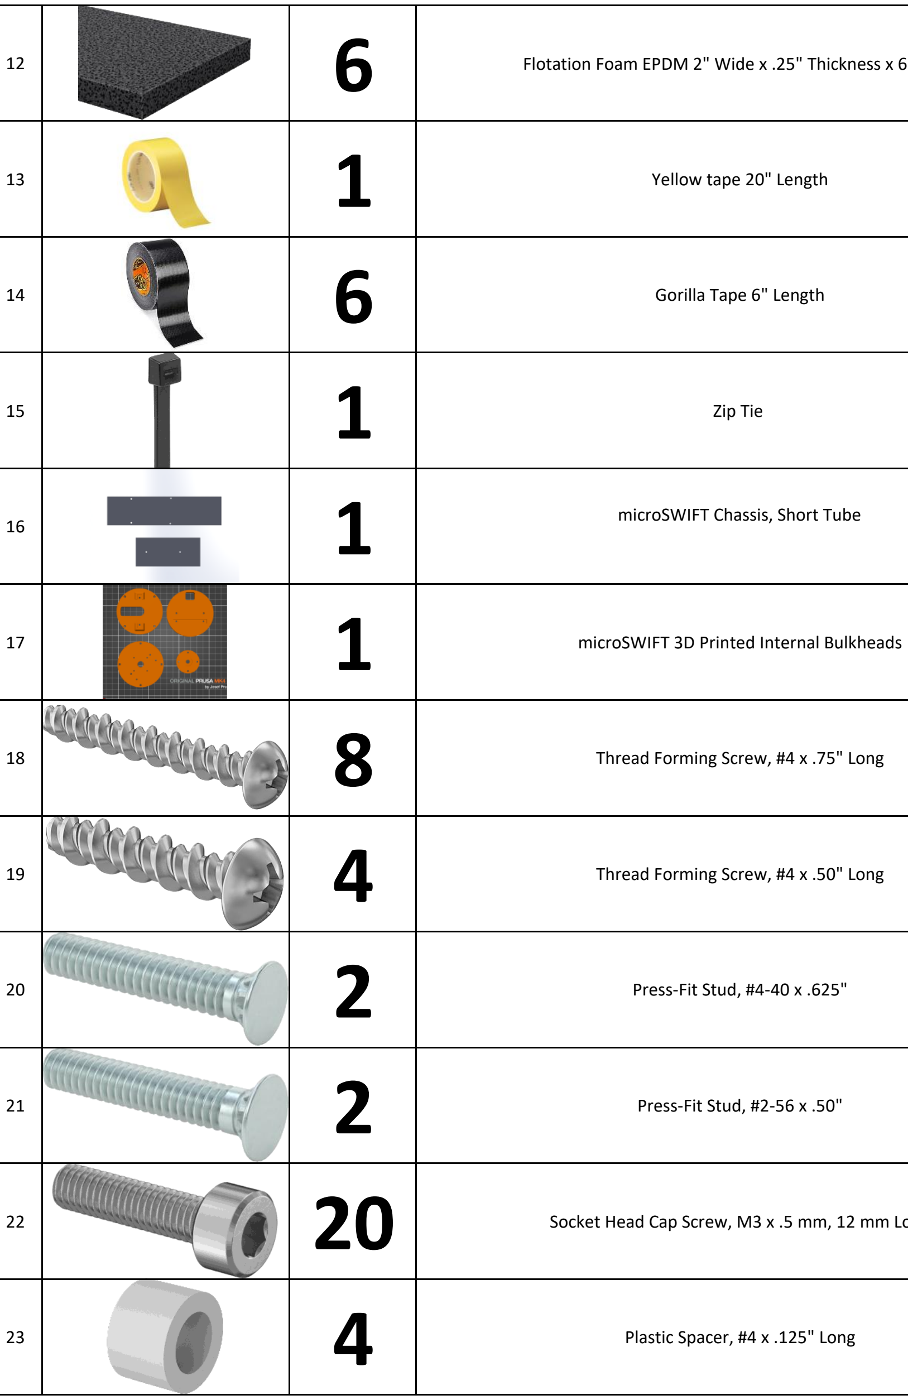
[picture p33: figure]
Yellow tape 20" Length; Gorilla Tape 6" Length; Zip Tie; microSWIFT Chassis, Short Tube; microSWIFT 3D Printed Internal Bulkheads; Press-Fit Stud, #4-40 x .625"; Press-Fit Stud, #2-56 x .50"; Plastic Spacer, #4 x .125" Long

12 | 6 | Flotation Foam EPDM 2" Wide x .25" Thickness x 6" Long
18 | 8 | Thread Forming Screw, #4 x .75" Long
19 | 4 | Thread Forming Screw, #4 x .50" Long
22 | 20 | Socket Head Cap Screw, M3 x .5 mm, 12 mm Long


24 | 2 | Plastic Spacer, #2 x 5 mm Long
25 | 4 | Plastic Spacer, #4 x .4375" Long
26 | 4 | Socket Head Cap Screw, #4-40 x 1.25"

#2-56 Nut; #2 Internal Tooth Lock Washer

27 | 6 | #4-40 Lock Nut With Integrated Washer
30 | 2 | Connector Header Through Hole 70 Position 2x35
31 | 1 | Coaxial Cable Assembly SMA Right Angle Plug to SMA Jack


32 | 1 | Coaxial Cable Assembly SMA Right Angle Plug to SMA Plug
33 | 1 | Cable Assembly 10 Position Molex Picoblade Socket to Socket, 50 mm Long
34 | 1 | Connector Housing, Molex Micro-Fit 3.0 2 Position
35 | 2 | Connector Socket Contacts, Molex Micro-Fit 3.0


36 | 2 | Battery Holder, 4x C Cell
37 | 8 | C Battery Cell

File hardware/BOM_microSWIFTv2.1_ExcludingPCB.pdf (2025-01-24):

COMPONENT | DESCRIPTION | PART # | SUPPLIER | SUPPLIER PN
| Pkg Qty | Price | BOM

Major Components

QTY | COST
Microcontroller | NUCLEO-U575ZI-Q | Nucleo U575ZI-QMouser | 511-NUCLEO-U575ZI-Q | 1 | 24.46 $ | 1 | 24.46 $
Iridium Modem | RockBLOCK 9603 SBD modem | 9603 | Ground Control | SKU: FP-RB-9603 | 1 | 302.00 $ | 1
microSWIFT PCB (Separate BOM sheet) | APL design | - | - | - | 1 | | 1
Antenna, GPS/Iridium | Maxtenna M1600HCT-P-SMA | M1600HCT-P-SMAouser | 259-M1600HCT-P-SMA | 1 | 64.00 $ | 1 | 64.00 $
Sensor Payloads
Aanderaa 4319B CT sensor | Aanderaa Conductivity/Temp sensor | 5819C | Xylem | 5819C | 1 | $2,972 | 1 | 2,972.00 $
TSYS01 Temp Sensor | Blue Robotics TSYS01 Temp Sensor | BR-100317 | Blue Robotics | BR-100317 | 1 | 70.00 $ | 1 | 70.00 $

Housing
Main housing tube, Long | 17.75" Long custom made cast acrylic | 8486K565 | McMaster-Carr | 8486K565 | 2 | 296.40 $ | 1 | 148.20 $
Main housing tube, Short | Blue Robotics 15.6" cast acrylic | BR-100293 | Blue Robotics | BR-100293 | 1 | 262.00 $ | 1 | 262.00 $
O-ring flanges (with tab) | 3" | WTE3-M-LOCKING-FLANGE-SEAL-R1-RP Blue Robotics | WTE3-M-LOCKING-FLANGE-SEAL-R1-RP1 | 29.75 $ | 2 | 59.50 $
O-ring flanges (tab removed) | APL fab | - | APL | -
End cap top | Acrylic dome | WTE3-P-END-CAP-R1-RP Blue Robotics | WTE3-P-END-CAP-R1-RP | 1 | 27.20 $ | 1 | 27.20 $
End cap bottom | Acrylic flat | WTE3-P-DOME-R1-RP Blue Robotics | WTE3-P-DOME-R1-RP | 1 | 12.75 $ | 1 | 12.75 $
O-ring radial seal | Radial o-ring for 3" series flanges | 9452K157 | McMaster-Carr | 9452K157 | 50 | 12.99 $ | 4 | 1.04 $
O-ring face seal | Face o-ring for 3" series flanges | 9452K155 | McMaster-Carr | 9452K155 | 50 | 12.53 $ | 2 | 0.50 $
Sticker | APL sticker | - | Letters Unlimited - | 1 | 4.50 $ | 1 | 4.50 $
Interface connectors/cables
RF Cable assembly, antenna to board | Custom cable | - | Digi Key | - | 1 | 1 | 14.00 $
RF Cable assembly, Iridium modem to board | Custom cable | - | Digi Key | - | 1 | 1 | 14.00 $
Cable assembly, Iridium modem to board | Picoblade 10 pos | 151341000 | Digi Key | WM17198-ND | 1 | 5.62 $ | 1 | 5.62 $
Ribbon cable, CT cable assembly | CBL RIBN 6COND 0.05 GRAY 3.28' | 63910615521CABDigi Key | 732-11799-ND | 2 | 1.73 $ | 1 | 0.87 $
Connector, instrument side, CT cable assemblyCONN CIRC INSERT 10P SOLDER CUP | FFA.3S.310.ZLADigi Key | FFA.3S.310.ZLA-ND | 1 | 51.12 $ | 1 | 51.12 $
Connector board side, CT cable assembly | IDC receptacle 6 position | 61200623021 | Digi Key | 732-5443-ND | 1 | 1.67 $ | 1 | 1.67 $
Headers, STM board | 0.1" (2.54mm) headers 2x35
G-D | Mouser | 200-TSW13507GD | 1 | 5.18 $ | 2 | 10.36 $
Buoyancy Foam
Buoyancy foam collar | 6x 6" x 2" x .25" EPDM Foam | McMaster-Carr | 93725K116 | 50 | 93.51 $ | 2 | 3.7404
Zip Tie | .18" x 17" UV rated zip tie | McMaster-Carr | 7130K61 | 100 | 23.40 $ | 1 | 0.234
Yellow tape for foam collar | Yellow vinyl tape | 471 | Grainger | 15F765 | 1 | 34.28 $ | 0.03333 | 1.14 $
Backing tape for foam | Gorilla tape, 1.875" wide x 8" | 105629 | Grainger | 787ER2 | 135 | 17.02 $ | 6 | 0.76 $
Ballast, if no CT | 350 g lead shot | | Scuba.com | -

Chassis
Chassis/PCB Mount, Long Tube | Marine-Grade HDPE Bar 1/4" X 3" X 4 ft., Black | McMaster-Carr | 6644N171 | 3 | 9.55 $ | 1 | 3.18 $
Chassis/PCB Mount, Short Tube
Internal Bulkhead Parts (set) | PETG plastic 3D print

Fasteners
Screws, #4x0.75 thread forming | #4 x .75" thread forming screw | McMaster-Carr | 97349A418 | 100 | 7.38 $ | 8 | 0.59 $
Screws, #4x0.50 thread forming | #4 x 0.5" thread forming screw | McMaster-Carr | 97349A417 | 100 | 6.30 $ | 4 | 0.25 $
Socket head cap screw M3x12mm | 18-8 Stainless Steel Socket Head Screw, M3 x 0.5 mm Thread, 12 mm Long McMaster-Carr | 91292A114 | 100 | 6.00 $ | 20 | 1.20 $
Press fit stud, Battery holders to chassis | #4-40 x .625" | McMaster-Carr | 93580A010 | 50 | 9.48 $ | 4 | 0.76 $
Press fit stud, Iridium modem to board | #2-56 x 0.50 | McMaster-Carr | 93580A544 | 50 | 9.77 $ | 2 | 0.39 $
Spacers, Nucleo board to chassis | #4, 0.125" long | McMaster-Carr | 94639A702 | 100 | 13.05 $ | 4 | 0.52 $
Spacers Iridium modem to board | #2, 5mm (.197") long | 5243059905 | Digi Key | RPC3356-ND | 1 | 0.12 $ | 2 | 0.23 $
Spacers, microSWIFT to Nucleo board | #4, 7/16" long | McMaster-Carr | 90176A114 | 25 | 4.12 $ | 4 | 0.66 $
Screws, board stack to chassis | #4-40 x 1.25" SHC | McMaster-Carr | 92196A032 | 100 | 9.84 $ | 4 | 0.39 $
Alternative: #4-40 x 1.25" stud | #4-40 x 1.25" Press-Fit Stud | McMaster-Carr | 93580A552 | 25 | 11.93 $ | 4 | 1.91 $
Hex Nut w/ Lock Washer #4-40 | #4-40 hex nut with ingegrated lock washer | McMaster-Carr | 96278A005 | 100 | 9.23 $ | 8 | 0.74 $
Hex nut #2-56 | #2-56 hex nut | McMaster-Carr | 91841A003 | 100 | 3.90 $ | 2 | 0.08 $
Lock washer #2 | #2 external tooth lock washer | McMaster-Carr | 98449A500 | 100 | 3.25 $ | 2 | 0.07 $
Plastic washer, CT sensor | M16 | McMaster-Carr | 95610A640 | 25 | 12.90 $ | 2 | 1.03 $
Nut, CT sensor | M16 x 1.0 mm | McMaster-Carr | 90326A203 | 5 | 11.66 $ | 1 | 2.33 $
Adhesive mount, dessicant pack | 0.75" x .75" | McMaster-Carr | 7582K11 | 50 | 13.33 $ | 1 | 0.27 $
Zip tie, dessicant pack | 6" Narrow zip tie | McMaster-Carr | 7130K42 | 100 | 6.05 $ | 1 | 0.06 $
Dessicant pack | 2 5/8" x 1" | McMaster-Carr | 3492T35 | 300 | 86.71 $ | 1 | 0.29 $
Battery
Battery holder | 4x C cell holder | BH24CW | Digi Key | BH24CW-ND | 1 | 2.67 $ | 2 | 5.35 $
Connector housing, battery wiring harness | CONN RCPT HSG 2POS 3.00MM | Digi Key | WM1845-ND | 1 | 0.40 $ | 1 | 0.40 $
Contacts, battery wiring harness | CONN SOCKET 20-24AWG CRIMP TIN | Digi Key | WM1837CT-ND | 1 | 0.13 $ | 1 | 0.13 $
Battery cells | C cell alkaline battery 1.5V | 04914, 4014, AM2, E93, LR14, MN1400 McMaster-Carr | 71455K63 | 72 | 76.08 | 8 | 8.45 $

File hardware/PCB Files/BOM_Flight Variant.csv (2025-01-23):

Line # | Name | Description | Designator | Quantity | Mount | Case/Package | Manufacturer 1 | Manufacturer Part Number 1 | Supplier 1 | Supplier Part Number 1
7 | PESD0402-140 | TVS DIODE 14VWM 40VC 0402 | D1 | 1 | Surface Mount | 0402 | Littelfuse | PESD0402-140 | Digikey | PESD0402-140CT-ND
45 | G3VM-61GR2(TR05) | Relay Ssr 25MA 1.48V Dc-in 1.3A 48V Ac/dc-out 4-PIN Sop T/r | K1 | 1 | Surface Mount | SOP | Omron | G3VM-61GR2(TR05) | Digikey | Z5431CT-ND
50 | LMR50410YFQDBVRQ1 | Automotive qualified SIMPLE SWITCHER 4-V to 36-V, 1-A synchronous step-down converter 6-SOT-23 -40 to 150 | U8, U9 | 2 | Surface Mount | SOT-23-6 | Texas Instruments | LMR50410XDBVR | Digikey | 296-LMR50410XDBVRDKR-ND
42 | SMAZ5V1-13-F | Vz=5.1V 4.84V~5.4V Izt=100mA P=1W | D5 | 1 | Surface Mount | SMA | Diodes | SMAZ5V1-13-F | Digikey | SMAZ5V1-FDIDKR-ND
39 | 43650-0229 | Conn Wire to Board HDR 2 POS 3mm Solder ST Top Entry Thru-Hole Micro-Fit 3.0 Tray | J1 | 1 | Through Hole | Header | Molex | 43650-0229 | Digikey | WM10662-ND
37 | SRR4028-3R9Y | Inductor Power Shielded Wirewound 3.9uH 30% 8.58 Q-Factor Ferrite 1.5A Saturation 60mROhm DCR | L1 | 1 | Surface Mount | 2020 | Bourns | SRR4028-3R9Y | Digikey | 118-SRR4028-3R9YCT-ND
38 | SRR4028-3R3Y | Inductor Power Shielded Wirewound 3.3uH 30% 7.72 Q-Factor Ferrite 1.65A Saturation 35mROhm DCR | L2 | 1 | Surface Mount | 2020 | Bourns | SRR4028-3R3Y | Digikey | SRR4028-3R3YCT-ND
2 | MAX-M10S-00B | Gnss Lcc Rx, Rom, Tcxo, Lna, Saw | MD1 | 1 | Surface Mount | 18-SMD Module | u-blox | MAX-M10S-00B | Mouser | 377-MAX-M10S-00B
55 | NUCLEO-U575ZI-Q - uSwift REV 2.1 Variant | NUCLEO-U575ZI-Q - uSwift REV 2.1 Variant | MOD1 | 1
56 | RockBlock 9603 Iridum Modem | RockBlock 9603 Iridium Modem | MOD2 | 1
46 | IRLML2803TRPBF | Mosfet, Power; N-ch; Vdss 30V; Rds(on) 0.25 Ohm; Id 1.2A; MICRO3; Pd 540MW; Vgs +/-20V | Q1 | 1 | Surface Mount | SOT-23 | Infineon | IRLML2803TRPBF | Digikey | IRLML2803PBFCT-ND
47 | DMP3030SN-7 | Trans Mosfet P-ch 30V 0.7A 3-PIN SC-59 T/r / Mosfet P-ch 30V 700MA SC59-3 | Q2A, Q2B, Q4A, Q4B, Q4D, Q6, Q7 | 7 | Surface Mount | SOT-23-3 | Diodes | DMP3030SN-7 | Digikey | DMP3030SNDICT-ND
48 | DMN63D8L-7 | Trans Mosfet N-ch 30V 0.35A 3-PIN SOT-23 T/r | Q3A, Q3B, Q5A, Q5B, Q5D | 5 | Surface Mount | SOT-23-3 | Diodes | DMN63D8L-7 | Digikey | DMN63D8L-7DICT-ND
53 | MAX3221EIPWR | IC DRVR/RCVR RS232 1CH 16-TSSOP | U1 | 1 | Surface Mount | TSSOP | Texas Instruments | MAX3221EIPWR | Digikey | 296-19383-6-ND
54 | F2932NBGP | High Reliability SP2T Absorptive RF Switch | U2 | 1 | Surface Mount | VQFN | Renesas | F2932NBGP | Digikey | 800-3586-ND
49 | TPS70950QDBVRQ1 | LDO Regulator Pos 5V 0.15A 5-Pin SOT-23 T/R | U4 | 1 | Surface Mount | SOT-23-5 | Texas Instruments | TPS70950QDBVRQ1 | Digikey | 296-40935-1-ND
6 | CD40106BM96G4 | 6-ch, 3-V to 18-V inverters with Schmitt-Trigger inputs 14-SOIC -55 to 125 | U5 | 1 | Surface Mount | 14-SOIC | Texas Instruments | CD40106BM96G4 | Digikey | 296-31480-1-ND
52 | DRV5032AJLPG | Low power (5 Hz, <1µA), low voltage (up to 5.5V) switch 3-TO-92 -40 to 85. High sensitivity (9.5mT) Onmipolar operation. | U11, U12 | 2 | Through Hole | TO-92-3 | Texas Instruments | DRV5032AJLPG | Digikey | 296-DRV5032AJLPG-ND
8 | Capacitor 100nF +/- 10%, 50V, X7R, 0603 | Chip Capacitor, 100nF, +/- 10%, 50 V, X7R 0603 (1608 Metric) | C1, C2, C3, C4, C5, C8, C19, C20, C25, C27, C30, C32 | 12 | Surface Mount | 0603 | Yageo | CC0603KRX7R9BB104 | Digikey | 311-1344-6-ND
9 | Capacitor 100pF +/- 10%, 50V, X7R, 0603 | Chip Capacitor, 100pF, +/- 10%, 50 V, X7R 0603 (1608 Metric) | C6, C7 | 2 | Surface Mount | 0603 | Yageo | CC0603KRX7R9BB101 | Digikey | 311-3601-1-ND
3 | EEH-ZA1H100R | Cap Aluminum 10uF 50V 20% (5 X 5.8mm) SMD 0.12 Ohm 750mA 5000 hr 105°C Embossed T/R | C15, C18 | 2 | Surface Mount | Radial | Panasonic | EEH-ZA1H100R | Mouser | 667-EEH-ZA1H100R
34 | Capacitor 2.2uF 10%, 50V, X7R, 1210 | Chip Capacitor, 2.2uF, 10%, 50 V, X7R 1210 (3225 Metric) | C16, C17, C36, C37 | 4 | Surface Mount | 1210 | Yageo | CC1210KKX7R9BB225 | Digikey | 311-3535-1-ND
30 | Capacitor 330nF 10%, 50V, X7R, 0805 | Chip Capacitor, 330nF, 10%, 50 V, X7R 0805 (2012 Metric) | C21 | 1 | Surface Mount | 0805 | Yageo | CC0805KKX7R9BB334 | Digikey | 311-1888-1-ND
31 | Capacitor 33nF 10%, 50V, X7R, 0805 | Chip Capacitor, 33nF, 10%, 50 V, X7R 0805 (2012 Metric) | C24A, C24B, C35A, C35B, C35D | 5 | Surface Mount | 0805 | Yageo | CC0805KRX7R9BB333 | Digikey | 311-1374-1-ND
35 | Capacitor 10uF 10%, 50V, X7R, 1210 | Chip Capacitor, 10uF, 10%, 50 V, X7R 1210 (3225 Metric) | C26, C28, C29, C31, C33, C34, C44, C45 | 8 | Surface Mount | 1210 | Yageo | CC1210KKX7R9BB106 | Digikey | 311-2035-6-ND
10 | Capacitor 10nF +/- 5%, 50V, C0G, 0603 | Chip Capacitor, 10nF, +/- 5%, 50 V, C0G 0603 (1608 Metric) | C38, C39 | 2 | Surface Mount | 0603 | Yageo | CC0603JRNPO9BN103 | Digikey | 311-3960-1-ND
44 | 1N4148WS | Small Signal Diode, 75 V, 0.15 A, -55 to 150 degC, 2-Pin SOD-323, RoHS, Tape and Reel | D2, D3, D4, D6, D7 | 5 | Surface Mount | SOD-323 | ON Semiconductor / Fairchild | 1N4148WS | Digikey | 1N4148WSFSCT-ND
11 | LTST-C190GKT | LED Uni-Color Green, 100 mW, 30 mA, -55 to 85 degC, 2-Pin SMD, RoHS, Tape and Reel | DS1 | 1 | Surface Mount | 0603 | Vishay Lite-On | LTST-C190GKT | Digikey | 160-1183-6-ND
12 | LTST-C190KRKT | LED Uni-Color Red, 62.5 mW, 25 mA, -30 to 85 degC, 2-Pin SMD, RoHS, Tape and Reel | DS2 | 1 | Surface Mount | 0603 | Vishay Lite-On | LTST-C190KRKT | Digikey | 160-1436-6-ND
43 | 5-1814832-2 | SMA Connector Jack, Female Socket 50Ohm Through Hole Solder | J2, J3 | 2 | Through Hole | SMA | TE Connectivity AMP | 5-1814832-2 | Digikey | 17-5-1814832-2CT-ND
40 | 61200621621 | Conn Shrouded Header (4 Sides) M 6 POS 2.54mm Solder ST Top Entry Thru-Hole Tray | J4 | 1 | Through Hole | Header | Wurth Electronics | 61200621621 | Digikey | 732-5394-ND
1 | SSW-135-02-G-D | Tiger Buy™ Socket Strip with PCB Tails, 0.100" Pitch | J5, J6 | 2 | Through Hole | Header | Samtec | SSW-135-02-G-D | Newark | 11P9882
41 | 53398-4010 | Conn Shrouded Header (3 Sides) HDR 10 POS 1.25mm Solder ST Top Entry SMD GOLD Plating PicoBlade™ T/R | P1 | 1 | Surface Mount | Header | Molex | 0533984010 | Digikey | 900-0533984010CT-ND
32 | Resistor 0R +/- 1% 0805 125 mW | Chip Resistor, 0 Ohm, +/- 1%, 125 mW, -55 to 155 degC, 0805 (2012 Metric) | R2, R3 | 2 | Surface Mount | 0805 | Vishay | CRCW08050000Z0EA | Digikey | 541-0.0ACT-ND
13 | Resistor 499R +/-1% 0603 100 mW | Chip Resistor, 499 Ohm, +/- 1%, 0.1 W, -55 to 155 degC, 0603 (1608 Metric) | R6, R54 | 2 | Surface Mount | 0603 | Panasonic | ERJ-3EKF4990V | Digikey | P499HDKR-ND
14 | Resistor 100R +/-1% 0603 100 mW | Chip Resistor, 100 Ohm, +/- 1%, 0.1 W, -55 to 155 degC, 0603 (1608 Metric) | R7, R8 | 2 | Surface Mount | 0603 | Panasonic | ERJ-3EKF1000V | Digikey | P100HDKR-ND
15 | Resistor 10k +/-1% 0603 100 mW | Chip Resistor, 10 KOhm, +/- 1%, 01 W, -55 to 155 degC, 0603 (1608 Metric) | R11, R12, R26, R39A, R39B, R50, R51, R52, R53, R57A, R57B, R58A, R58B, R58D | 14 | Surface Mount | 0603 | Yageo | RC0603FR-0710KL | Digikey | 311-10.0KHRDKR-ND
16 | Resistor 0R +/- 5% 0603 100 mW | Chip Resistor, 0 Ohm, 0.1 W, -55 to 155 degC, 0603 (1608 Metric) | R24, R29, R31, R34, R55 | 5 | Surface Mount | 0603 | Yageo | RC0603JR-070RL | Digikey | 311-0.0GRCT-ND
17 | Resistor 649R +/-1% 0603 100 mW | Chip Resistor, 649 Ohm, +/- 1%, 0.1 W, -55 to 155 degC, 0603 (1608 Metric) | R23 | 1 | Surface Mount | 0603 | Panasonic | ERJ-3EKF6490V | Digikey | P649HCT-ND
18 | Resistor 24K9 +/-1% 0603 100 mW | Chip Resistor, 24.9k Ohm, +/- 1%, 0.1 W, -55 to 155 degC, 0603 (1608 Metric) | R25, R30 | 2 | Surface Mount | 0603 | Panasonic | ERJ-3EKF2492V | Digikey | P24.9KHCT-ND
19 | Resistor 221K +/-1% 0603 100 mW | Chip Resistor, 221k Ohm, +/- 1%, 0.1 W, -55 to 155 degC, 0603 (1608 Metric) | R27, R28, R32, R33 | 4 | Surface Mount | 0603 | Panasonic | ERJ-3EKF2213V | Digikey | P221KHCT-ND
20 | Resistor 649K +/-1% 0603 100 mW | Chip Resistor, 649k Ohm, +/- 1%, 0.1 W, -55 to 155 degC, 0603 (1608 Metric) | R35 | 1 | Surface Mount | 0603 | Panasonic | ERJ-3EKF6493V | Digikey | P649KHCT-ND
21 | Resistor 100K +/-1% 0603 100 mW | Chip Resistor, 100k Ohm, +/- 1%, 0.1 W, -55 to 155 degC, 0603 (1608 Metric) | R36 | 1 | Surface Mount | 0603 | Panasonic | ERJ-3EKF1003V | Digikey | P100KHDKR-ND
33 | Resistor 20m +/- 1% 0805 250 mW | Chip Resistor, 20 mOhm, +/- 1%, 125 mW, -55 to 125 degC, 0805 (2012 Metric) | R37 | 1 | Surface Mount | 0805 | Yageo | RL0805FR-7W0R02L | Digikey | 311-.02LUCT-ND
22 | Resistor 499K +/-1% 0603 100 mW | Chip Resistor, 499k Ohm, +/- 1%, 0.1 W, -55 to 155 degC, 0603 (1608 Metric) | R38A, R38B | 2 | Surface Mount | 0603 | Panasonic | ERJ-3EKF4993V | Digikey | P499KHCT-ND
23 | Resistor 1M +/-1% 0603 100 mW | Chip Resistor, 1M Ohm, +/- 1%, 0.1 W, -55 to 155 degC, 0603 (1608 Metric) | R40, R44 | 2 | Surface Mount | 0603 | Panasonic | ERJ-3EKF1004V | Digikey | P1.00MHDKR-ND
24 | Resistor 88K7 +/-1% 0603 100 mW | Chip Resistor, 88.7k Ohm, +/- 1%, 0.1 W, -55 to 155 degC, 0603 (1608 Metric) | R41 | 1 | Surface Mount | 0603 | Panasonic | ERJ-3EKF8872V | Digikey | P88.7KHCT-ND
25 | Resistor 200K +/-1% 0603 100 mW | Chip Resistor, 200k Ohm, +/- 1%, 0.1 W, -55 to 155 degC, 0603 (1608 Metric) | R42, R46 | 2 | Surface Mount | 0603 | Panasonic | ERJ-3EKF2003V | Digikey | P200KHDKR-ND
26 | Resistor 22K1 +/-1% 0603 100 mW | Chip Resistor, 22.1k Ohm, +/- 1%, 0.1 W, -55 to 155 degC, 0603 (1608 Metric) | R43, R47 | 2 | Surface Mount | 0603 | Panasonic | ERJ-3EKF2212V | Digikey | P22.1KHDKR-ND
27 | Resistor 51K1 +/-1% 0603 100 mW | Chip Resistor, 51.1k Ohm, +/- 1%, 0.1 W, -55 to 155 degC, 0603 (1608 Metric) | R45 | 1 | Surface Mount | 0603 | Panasonic | ERJ-3EKF5112V | Digikey | P51.1KHCT-ND
28 | Resistor 49K9 +/-1% 0603 100 mW | Chip Resistor, 49.9k Ohm, +/- 1%, 0.1 W, -55 to 155 degC, 0603 (1608 Metric) | R48A, R48B, R48D | 3 | Surface Mount | 0603 | Panasonic | ERJ-3EKF4992V | Digikey | P49.9KHDKR-ND
29 | Resistor 1k +/-1% 0603 100 mW | Chip Resistor, 1 KOhm, +/-1%, 0.1 W, -55 to 155 degC, 0603 (1608 Metric) | R49A, R49B, R49D | 3 | Surface Mount | 0603 | Yageo | RC0603FR-131KL | Digikey | 13-RC0603FR-131KLDKR-ND
51 | MCP1792-5002H/DB | High input voltage regulator 5.0 V 3Ld SOT-223 3 SOT-223 TUBE RoHS Compliant: Yes | U10 | 1 | Surface Mount | SOT-223-3 | Microchip | MCP1792-5002H/DB | Digikey | MCP1792-5002H/DB-ND
5 | TLV9061IDBVR | Single, 5.5-V, 10-MHz, RRIO operational amplifier for cost-optimized applications 5-SOT-23 -40 to 125 | U6 | 1 | Surface Mount | SOT-23-5 | Texas Instruments | TLV9061IDBVR | Digikey | 296-52284-1-ND

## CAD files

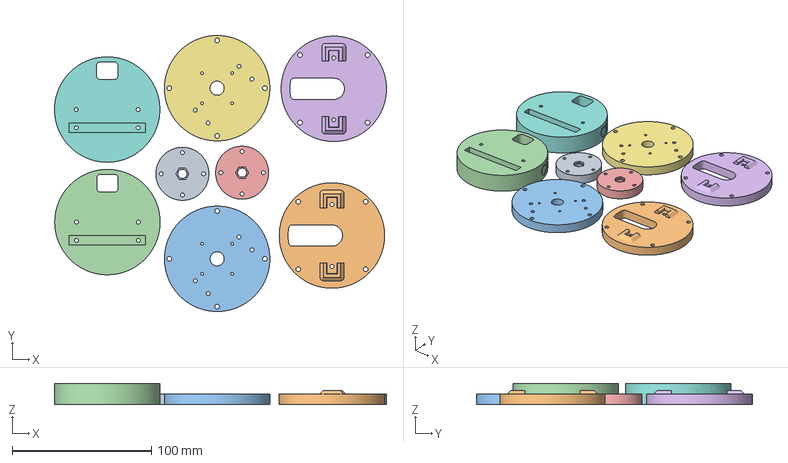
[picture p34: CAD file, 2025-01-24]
hardware/3D Print Files/Chassis Parts, PAIR, microSWIFTv2.1_PrusaMK4.3mf
238.4 x 198.2 x 15.2 mm
Antenna Mount, microSWIFT v2 13Aug2024_LargeHex.STL x 2
Bulkhead support, microSWIFT v2, Bottom.STL x 2
Bulkhead Support, microSWIFT v2, Top.STL x 2
Bulkhead Support, microSWIFT, v2, Middle.STL x 2

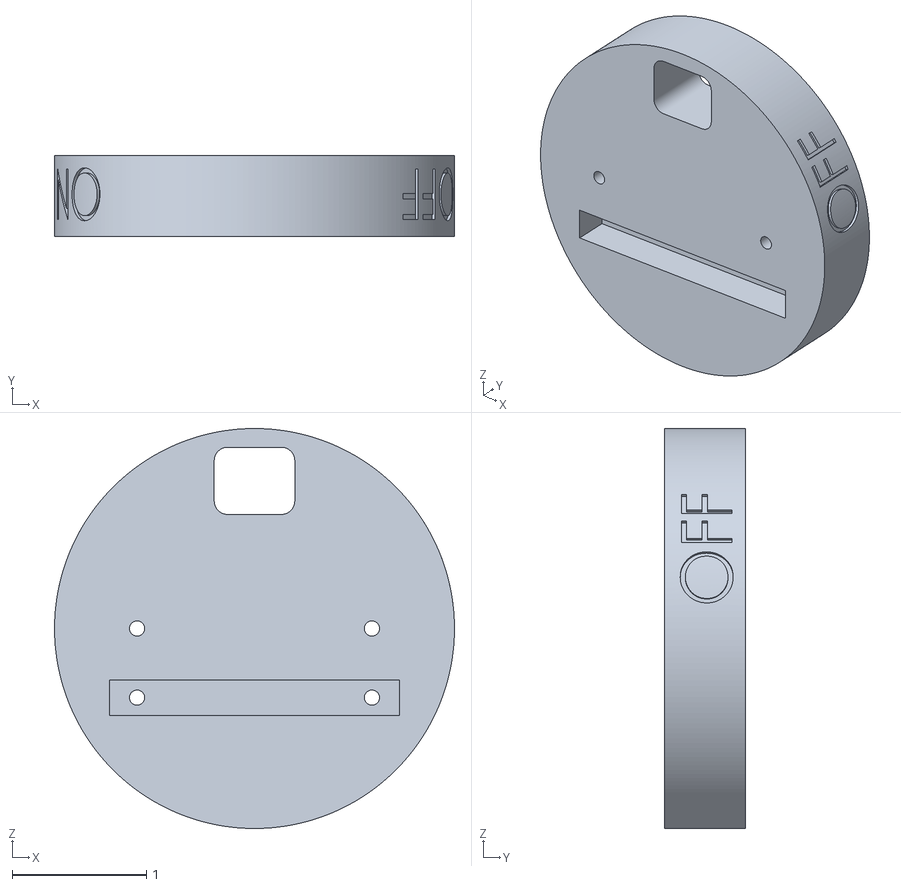
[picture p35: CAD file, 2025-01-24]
hardware/3D Print Files/Bulkhead Support, microSWIFT, v2, Middle.STL
2.98 x 0.6 x 2.98

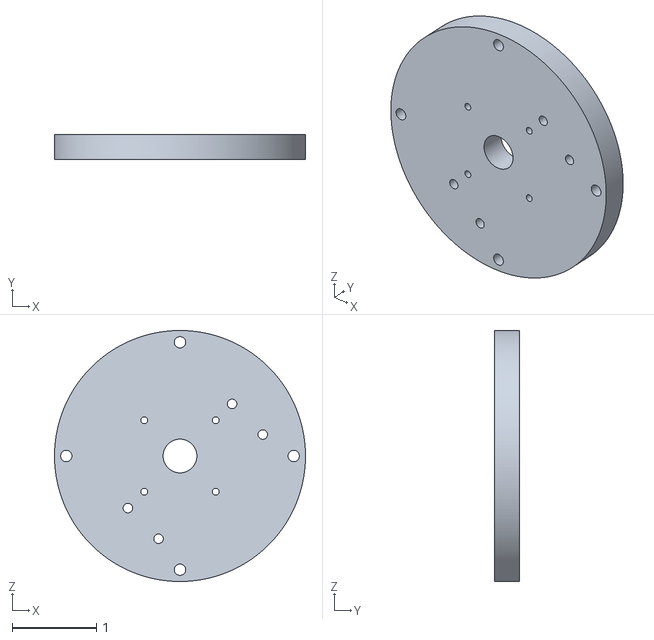
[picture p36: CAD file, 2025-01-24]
hardware/3D Print Files/Bulkhead Support, microSWIFT v2, Top.STL
2.98 x 0.3 x 2.98

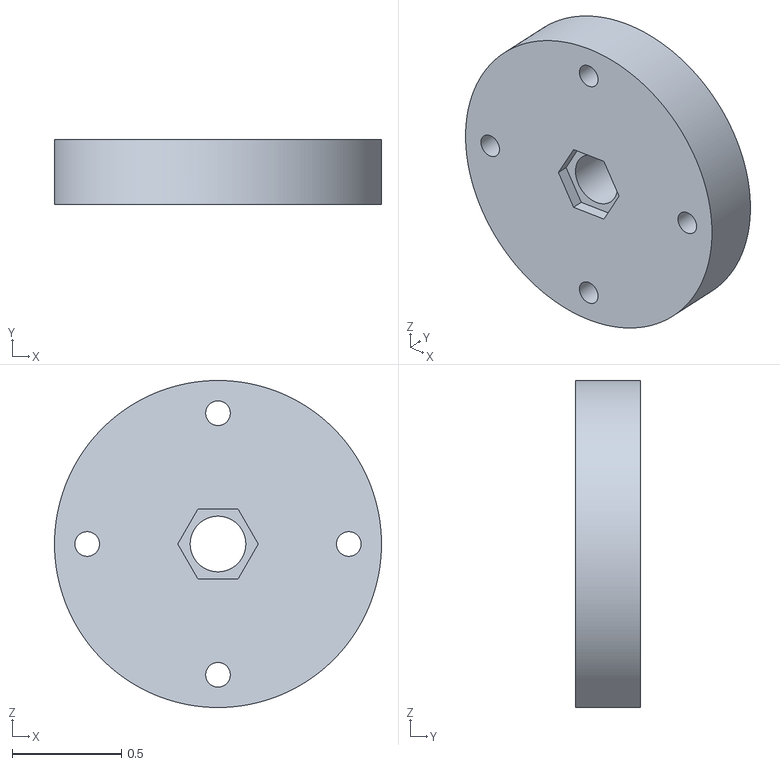
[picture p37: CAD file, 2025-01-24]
hardware/3D Print Files/Antenna Mount, microSWIFT v2 13Aug2024_LargeHex.STL
1.50 x 0.3 x 1.50

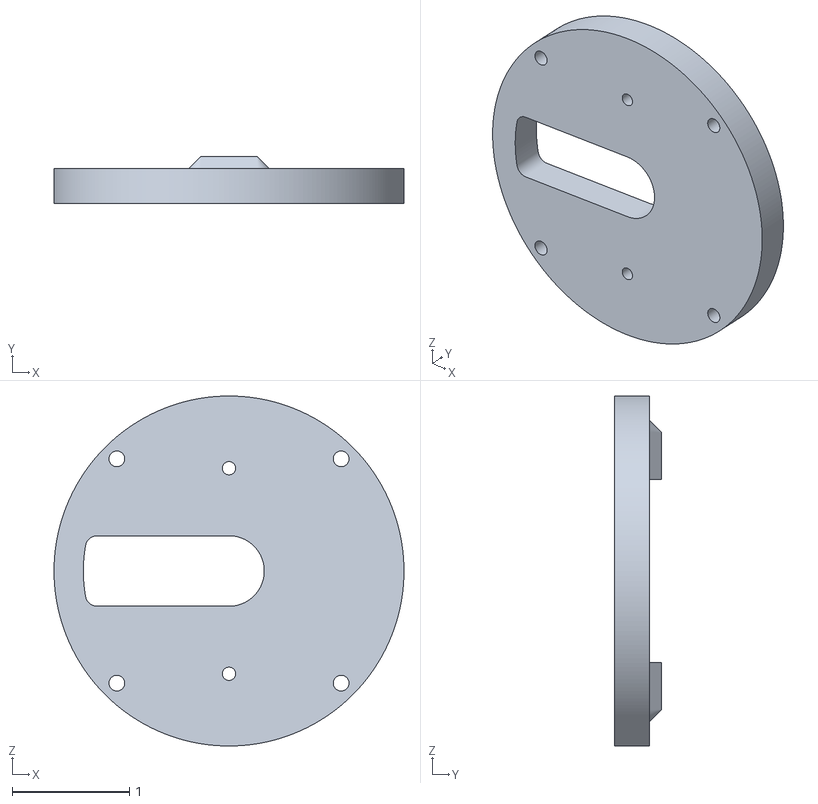
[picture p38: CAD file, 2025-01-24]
hardware/3D Print Files/Bulkhead support, microSWIFT v2, Bottom.STL
2.98 x 0.4 x 2.98

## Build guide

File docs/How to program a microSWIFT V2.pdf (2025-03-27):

# How to program a microSWIFT V2

## Download STM32CubeProgrammer

- Go to https://www.st.com/en/developmenttools/stm32cubeprog.html (https://www.st.com/en/development-tools/stm32cubeprog.html) (or just Google STM32CubeProgrammer) and download the correct version for your Operating System.
- You will need an ST account. Registration is quick and easy.

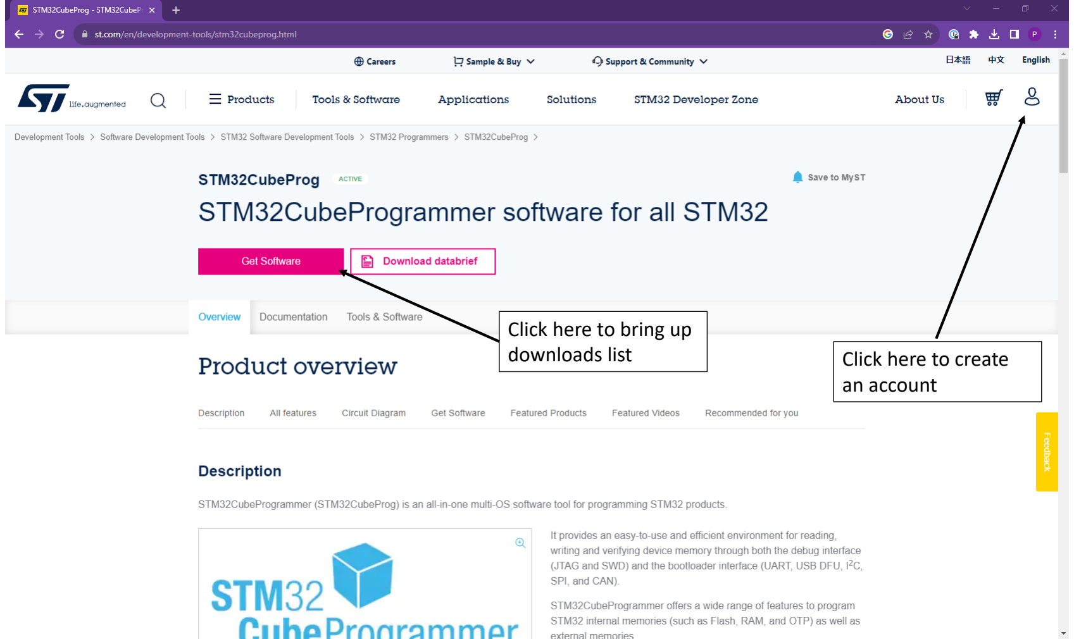
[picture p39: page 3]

Click here to bring up
downloads list | Click here to create
| an account

## Download the appropriate binaries

- All binaries are in the main branch of the microSWIFT-V2-Binaries repo within SASLabGroup organization: https://github.com/SASlabgroup/microSWIFT-V2-Binaries
- This repo is private – if you are unable to access this repo, speak to someone in SASLabGroup to have your github account added to the organization
- Binaries are file that end in the extension .elf, with the files named based on the deployment they are supporting

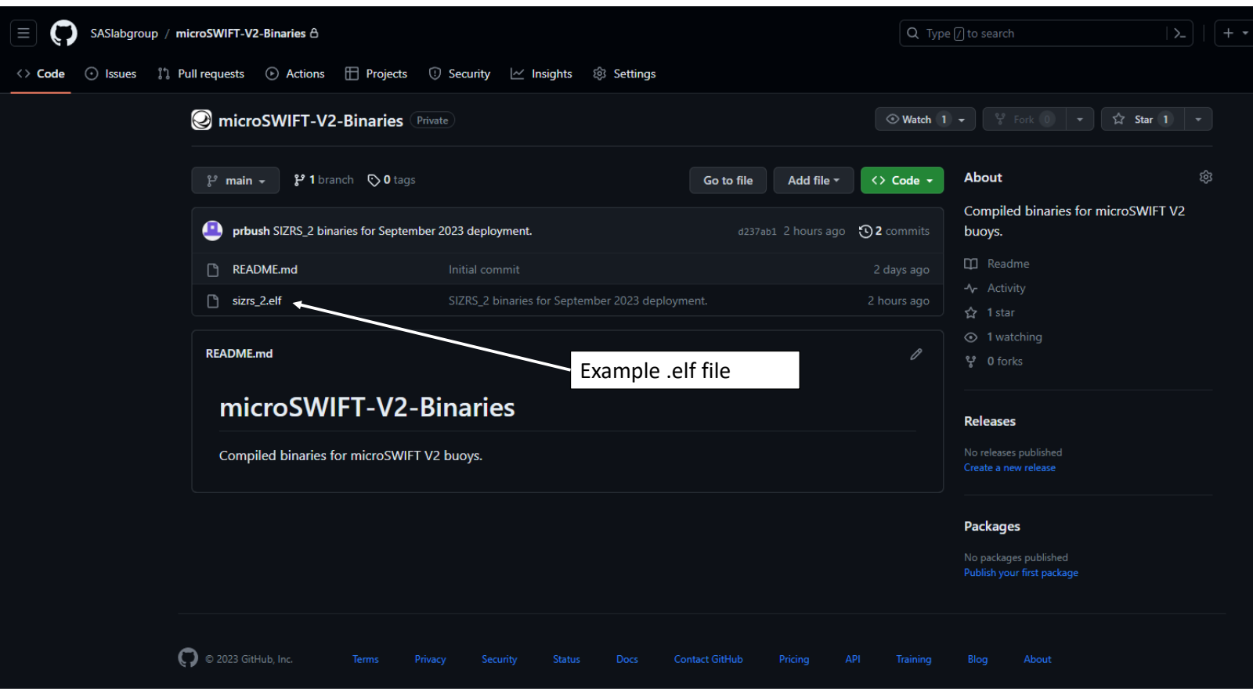
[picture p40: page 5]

Example .elf file

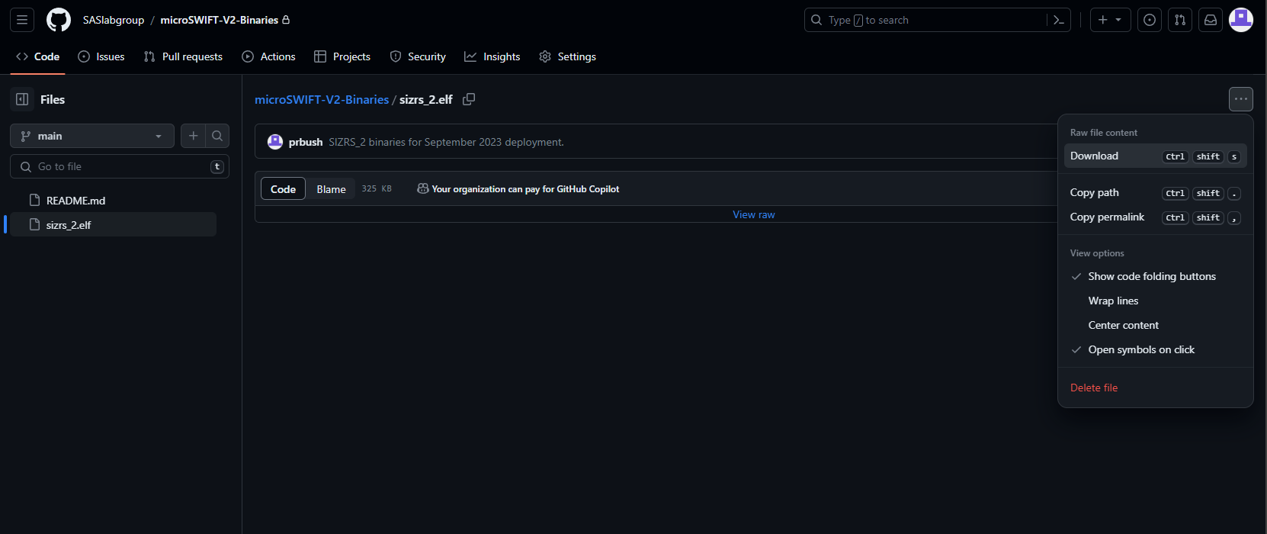
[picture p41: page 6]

Clicking on the file brings you to a page with an option to download the file

## Setting up STM32CubeProgrammer

- There are two options for programming the STM32 Nucleo boards:
1. Program the board directly using the onboard ST-Link. For this to work, solder bridge SB-1 must be connected. This is a good option with a fresh, straight out of the box board.
2. Program with external debugger. This is a great option when the microSWIFT V2 has already been assembled.

## Setting up with the onboard ST-Link

- When programming with the onboard ST-Link, you simply need to connect a micro USB to the board and program
- Prior to programming, verify the jumpers on the Nucleo board are in the correct configuration. The configuration straight out of the box is correct for this, as noted in the photo.

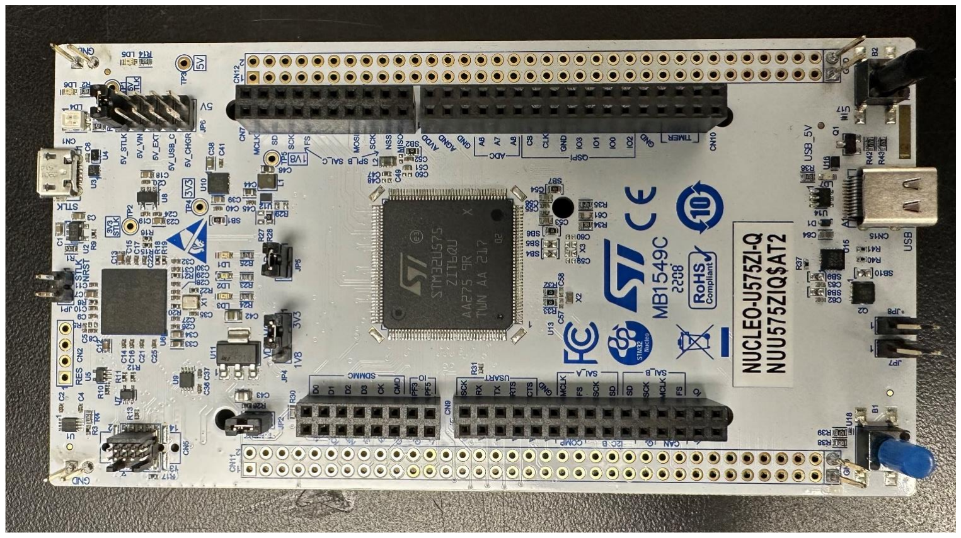
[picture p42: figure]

Micro USB port for
programming

## Setting up with an external debugger

- When programming an already assembled microSWIFT V2, use an external debugger and a power source, either battery pack or DC power supply
- Prior to programming, verify the jumpers on the Nucleo board are in the correct configuration

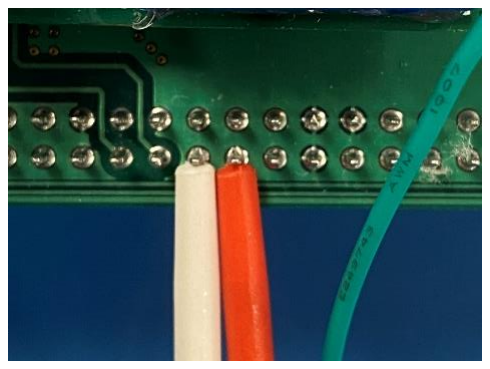
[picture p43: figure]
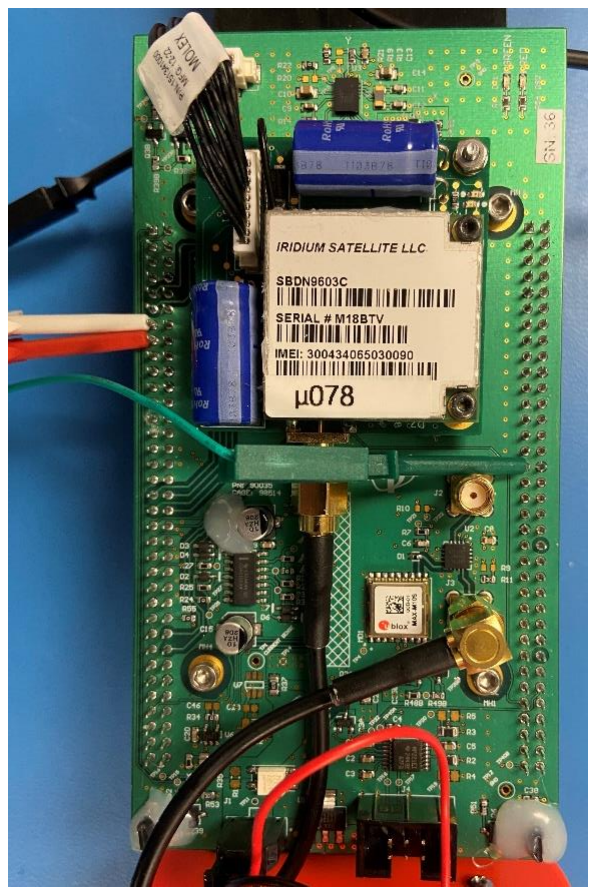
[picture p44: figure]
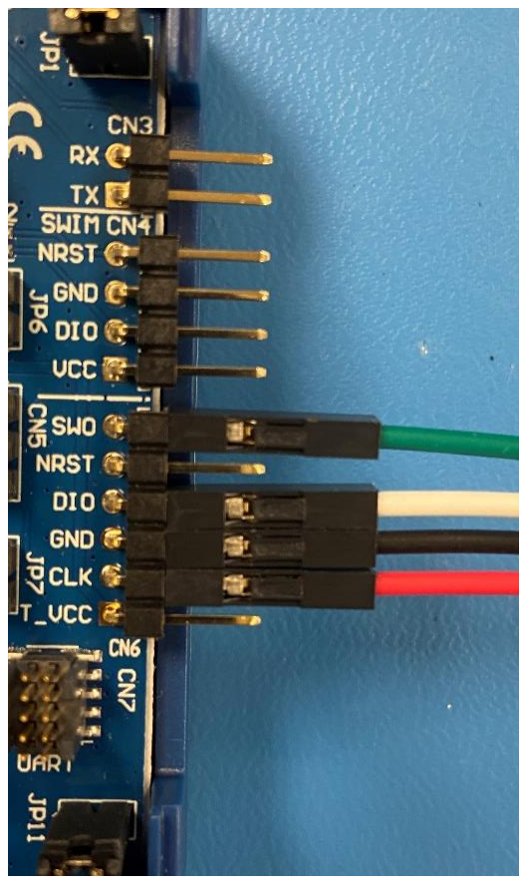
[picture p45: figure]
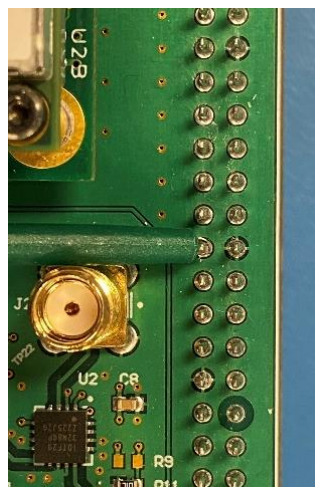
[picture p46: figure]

Pin assignments
(ST-Link → Nucleo):

SWO → PB3
DIO → PA13
GND → Nucleo Ground
CLK → PA14

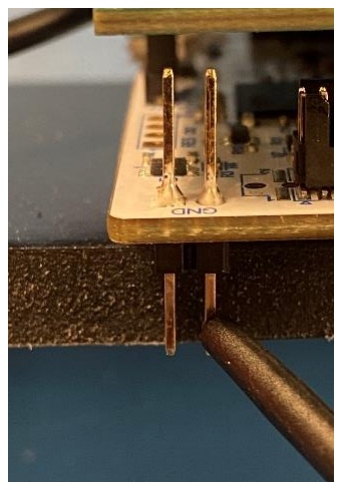
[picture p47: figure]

Pins are labelled on the
bottom of the Nucleo Board

## STM32CubeProgramming

- Open STM32CubeProgrammer
- Power on the microSWIFT
- Connect the ST-Link
- Click on the “Erasing and Programming” tab
- Set the filepath for the downloaded binaries
- Check the following boxes:
- Verify Programming
- Full Flash Memory checksum
- Run after programming
- Click on “Start Programming”

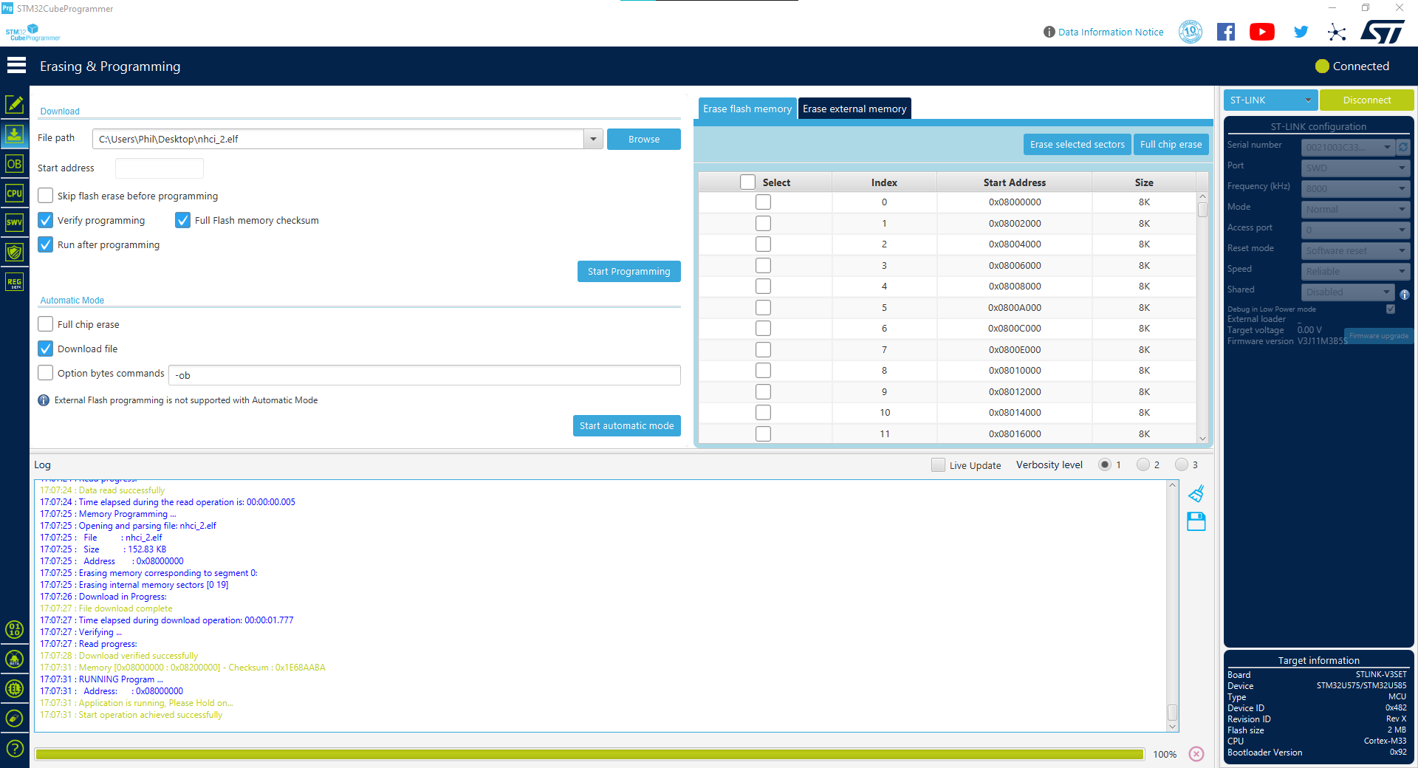
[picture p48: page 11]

## If it doesn’t work

- Verify that the connections are solid. It is easy for adjacent connections (PA13 and PA14 on Nucleo board) to touch
- Ensure you have powered on and then connected to the MCU
- Check that the ST-Link has a solid green light
- Check that jumpers on the Nucleo are correct

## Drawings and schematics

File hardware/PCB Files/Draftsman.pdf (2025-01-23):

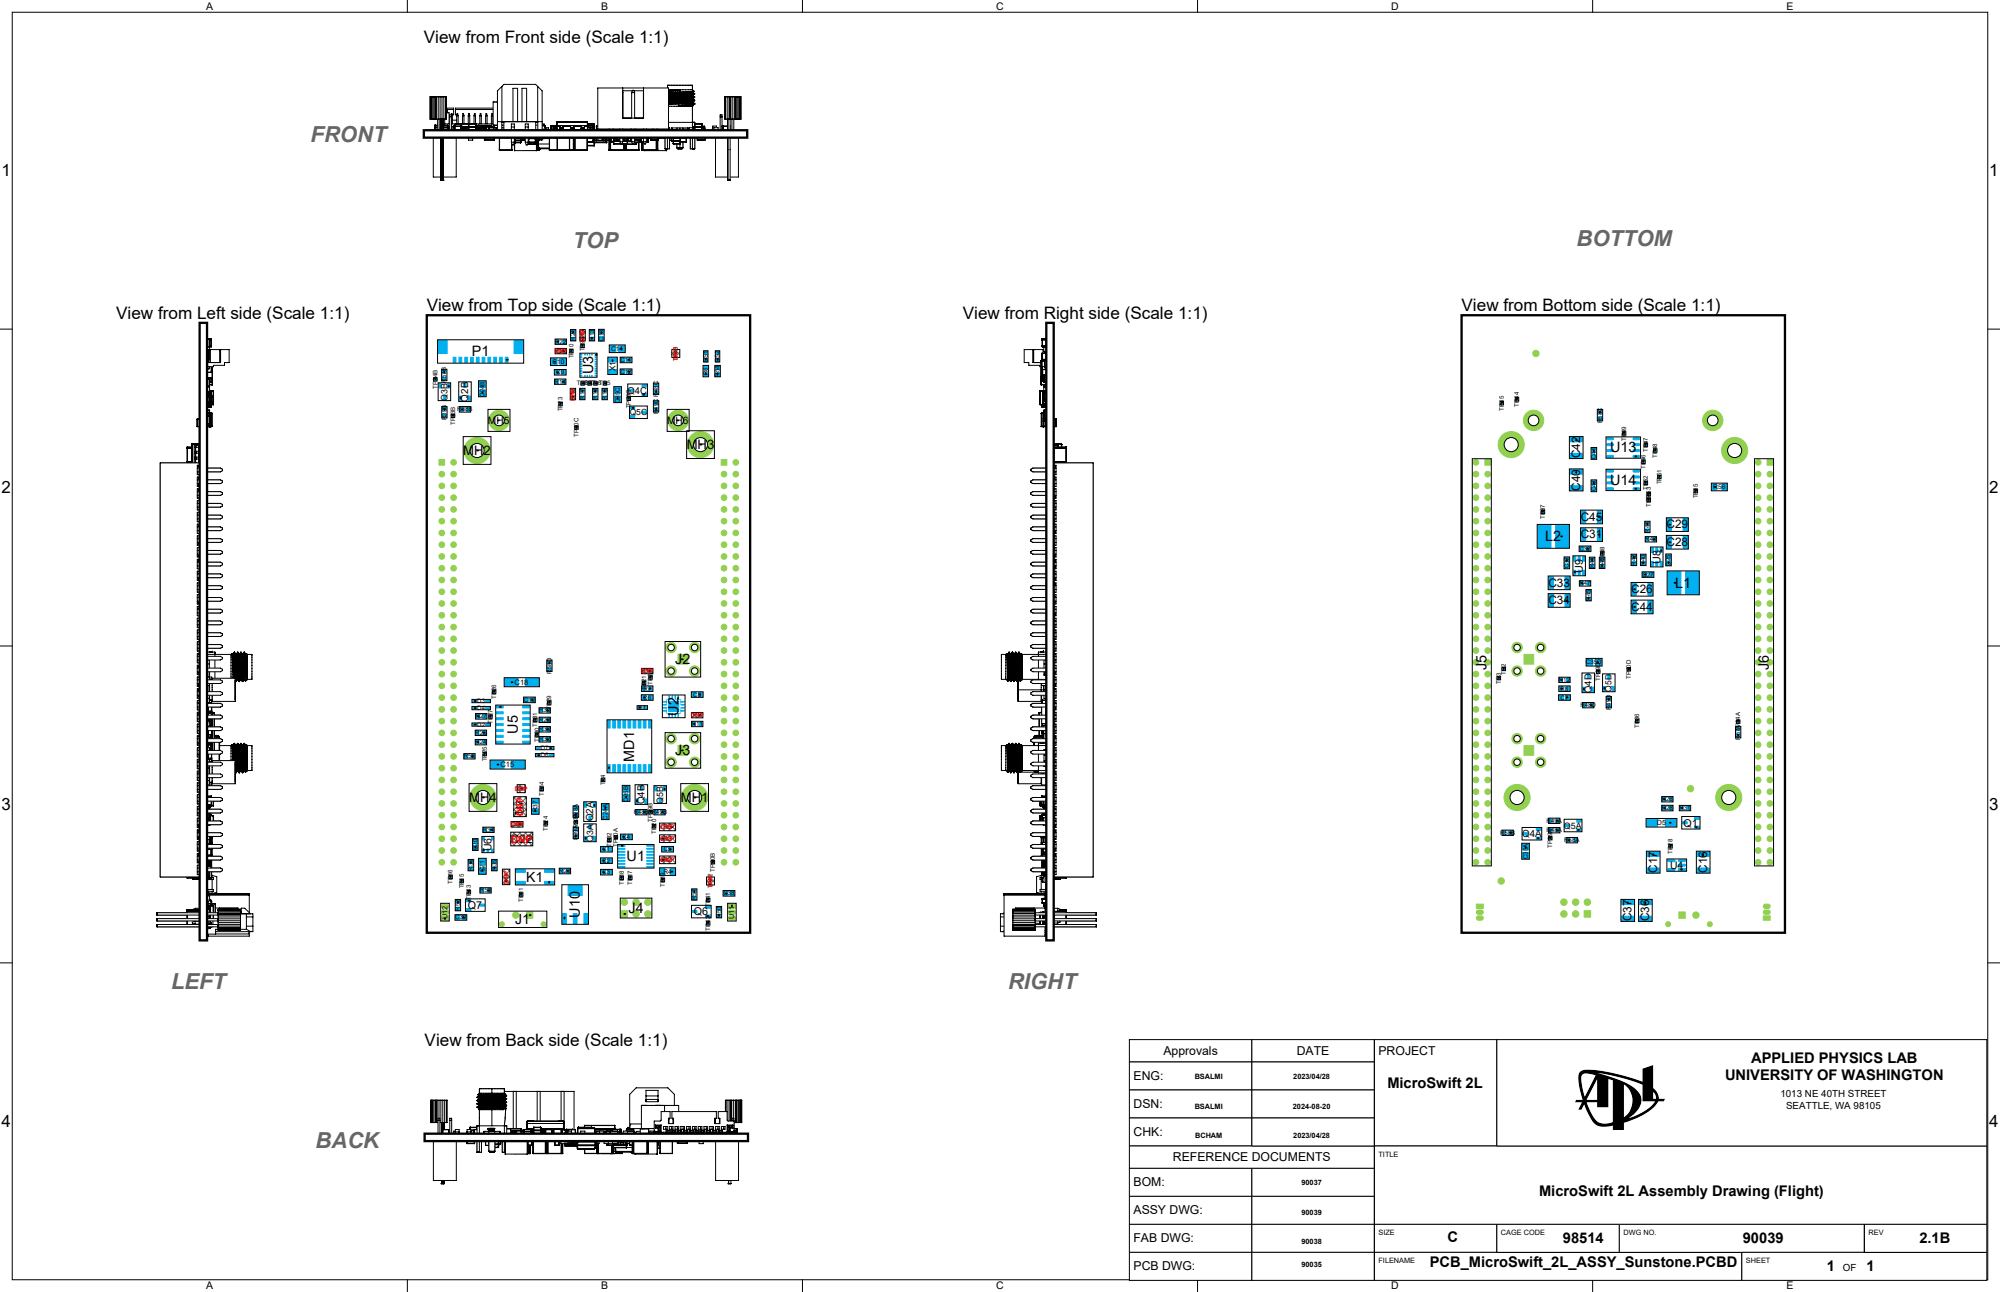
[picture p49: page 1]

View from Front side (Scale 1:1)

View from Top side (Scale 1:1)

View from Bottom side (Scale 1:1)

View from Back side (Scale 1:1)

MicroSwift 2L Assembly Drawing (Flight)

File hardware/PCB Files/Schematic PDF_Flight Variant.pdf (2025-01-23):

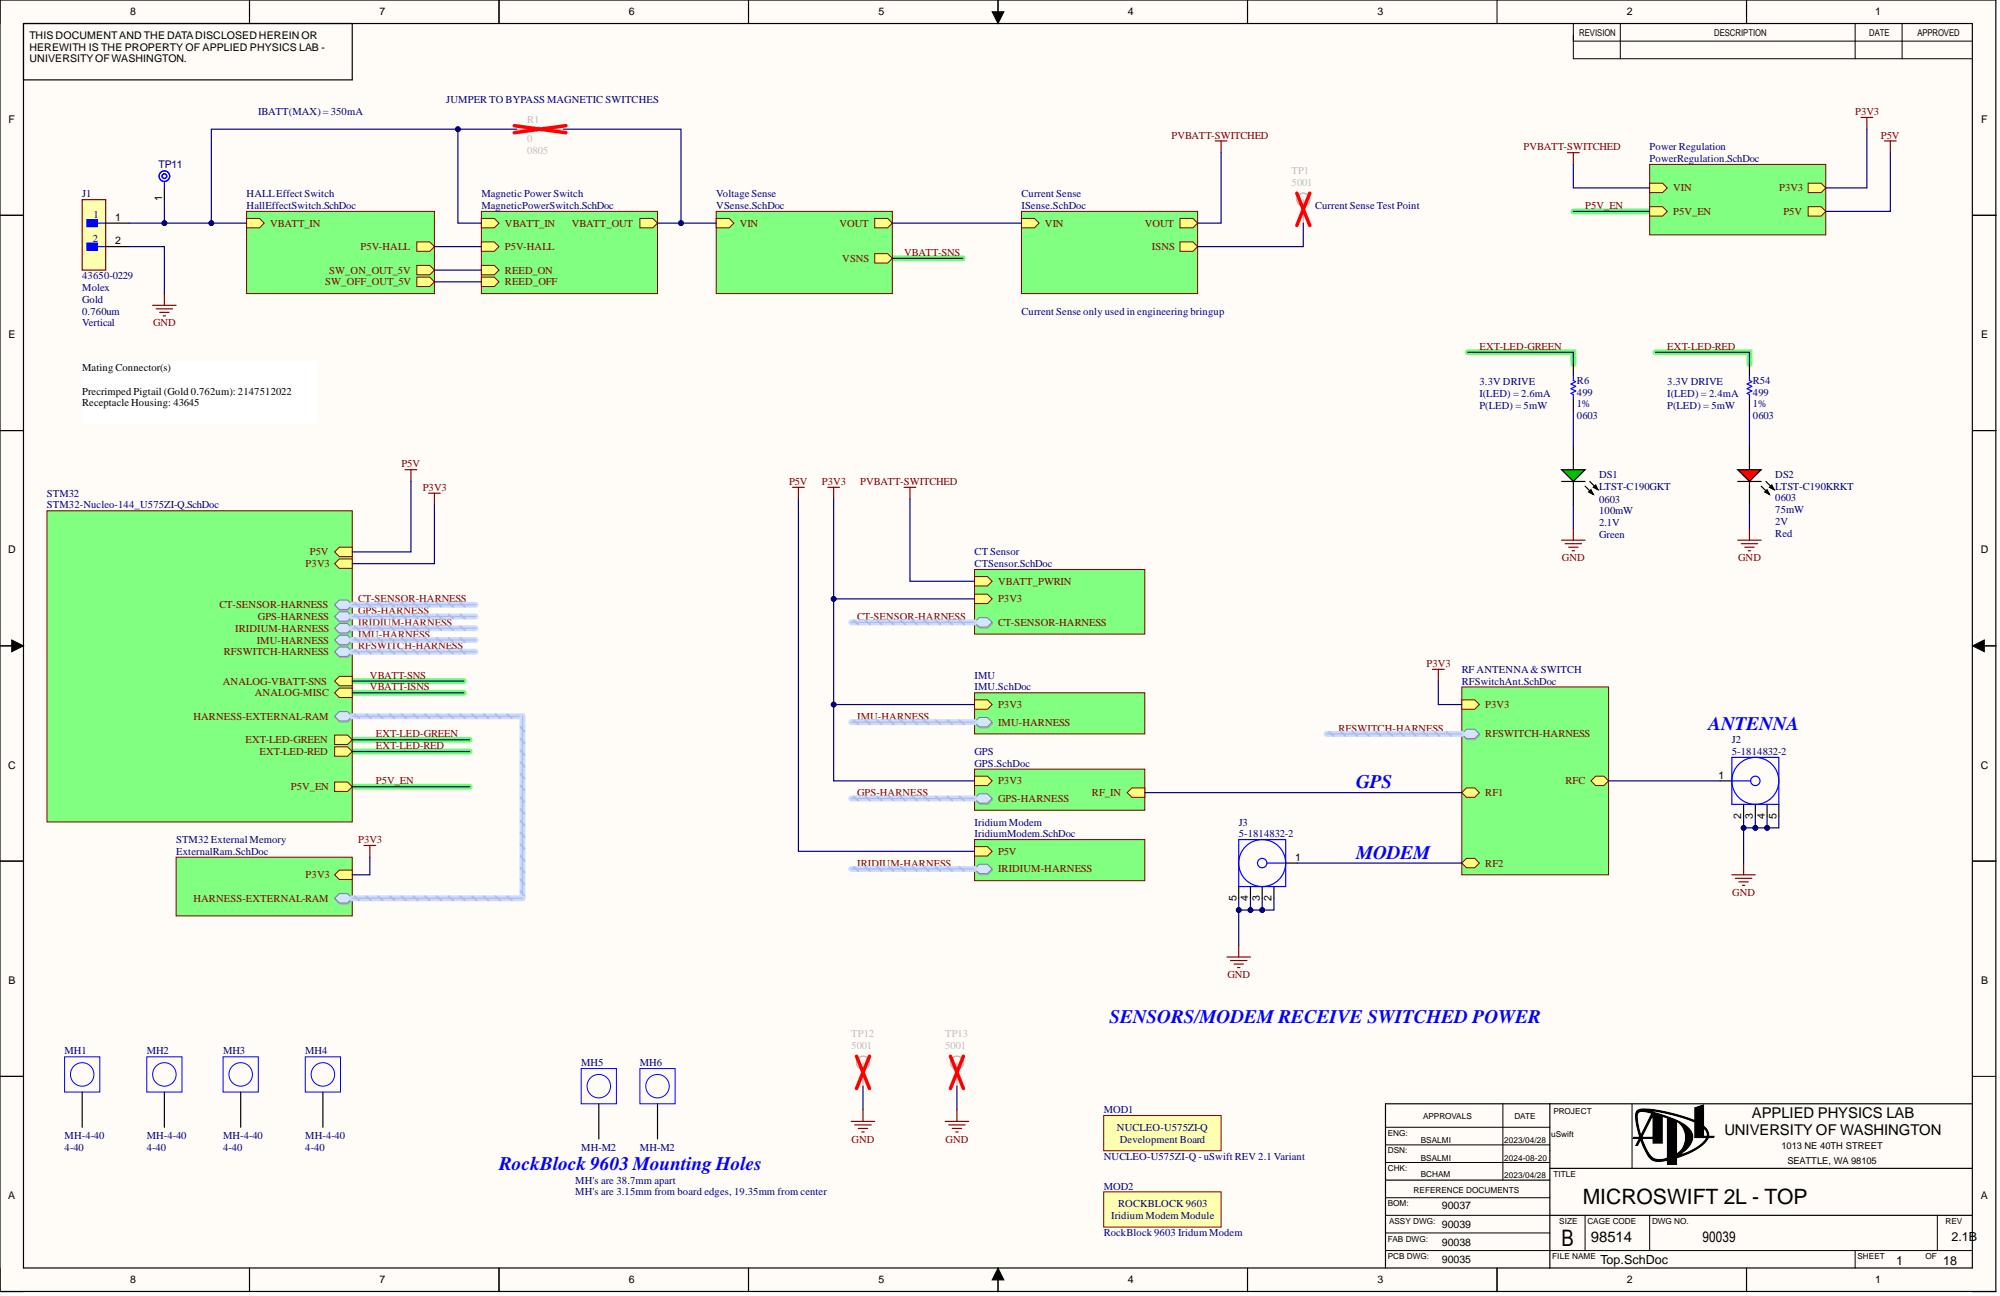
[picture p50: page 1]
HE PROPER; TY OF APPLIED PHYSI; CS LAB -; MICROSWIFT 2L -; 90039 Top.SchDoc; SIZE; DWG NO; FILE NAM; CAGE CODE; APPLIED PHYSI; CS LAB; REFERENCE DOCUMENTS; ASSY DWG; FAB DWG; PCB DWG; wer Reg; tage Sen; t Sen; CT Sen; A & SWITCH; Effect Sw; wer Sw; PASS MA; TIC SWITCH; MH's are; 5mm from; oard ed; 5mm from cen; Precrimped Pi; Green 2.1V 0603 DS1 LTST-C1; Red DS2 LTST-C1; ternal Memory; ift RE; dem Mo; 3 Iri

SENSORS/MODEM RECEIVE SWITCHED POWER TP1 5001

12 D | P5 V-H A LL SW _ O N _ O U T_ 5 V SW _ OFF_ O U T_ 5 V | P5 RE RE

GPS GPS.Sch

ENG : BSAL M I | 2 0 2 3/0 4/2 8

3 Mounting Holes MH's are 38.7mm apart

DSN: BSAL M I | 2 0 2 4-0 8-2 0

CHK: BCHAM | 2 0 2 3/0 4/2 8

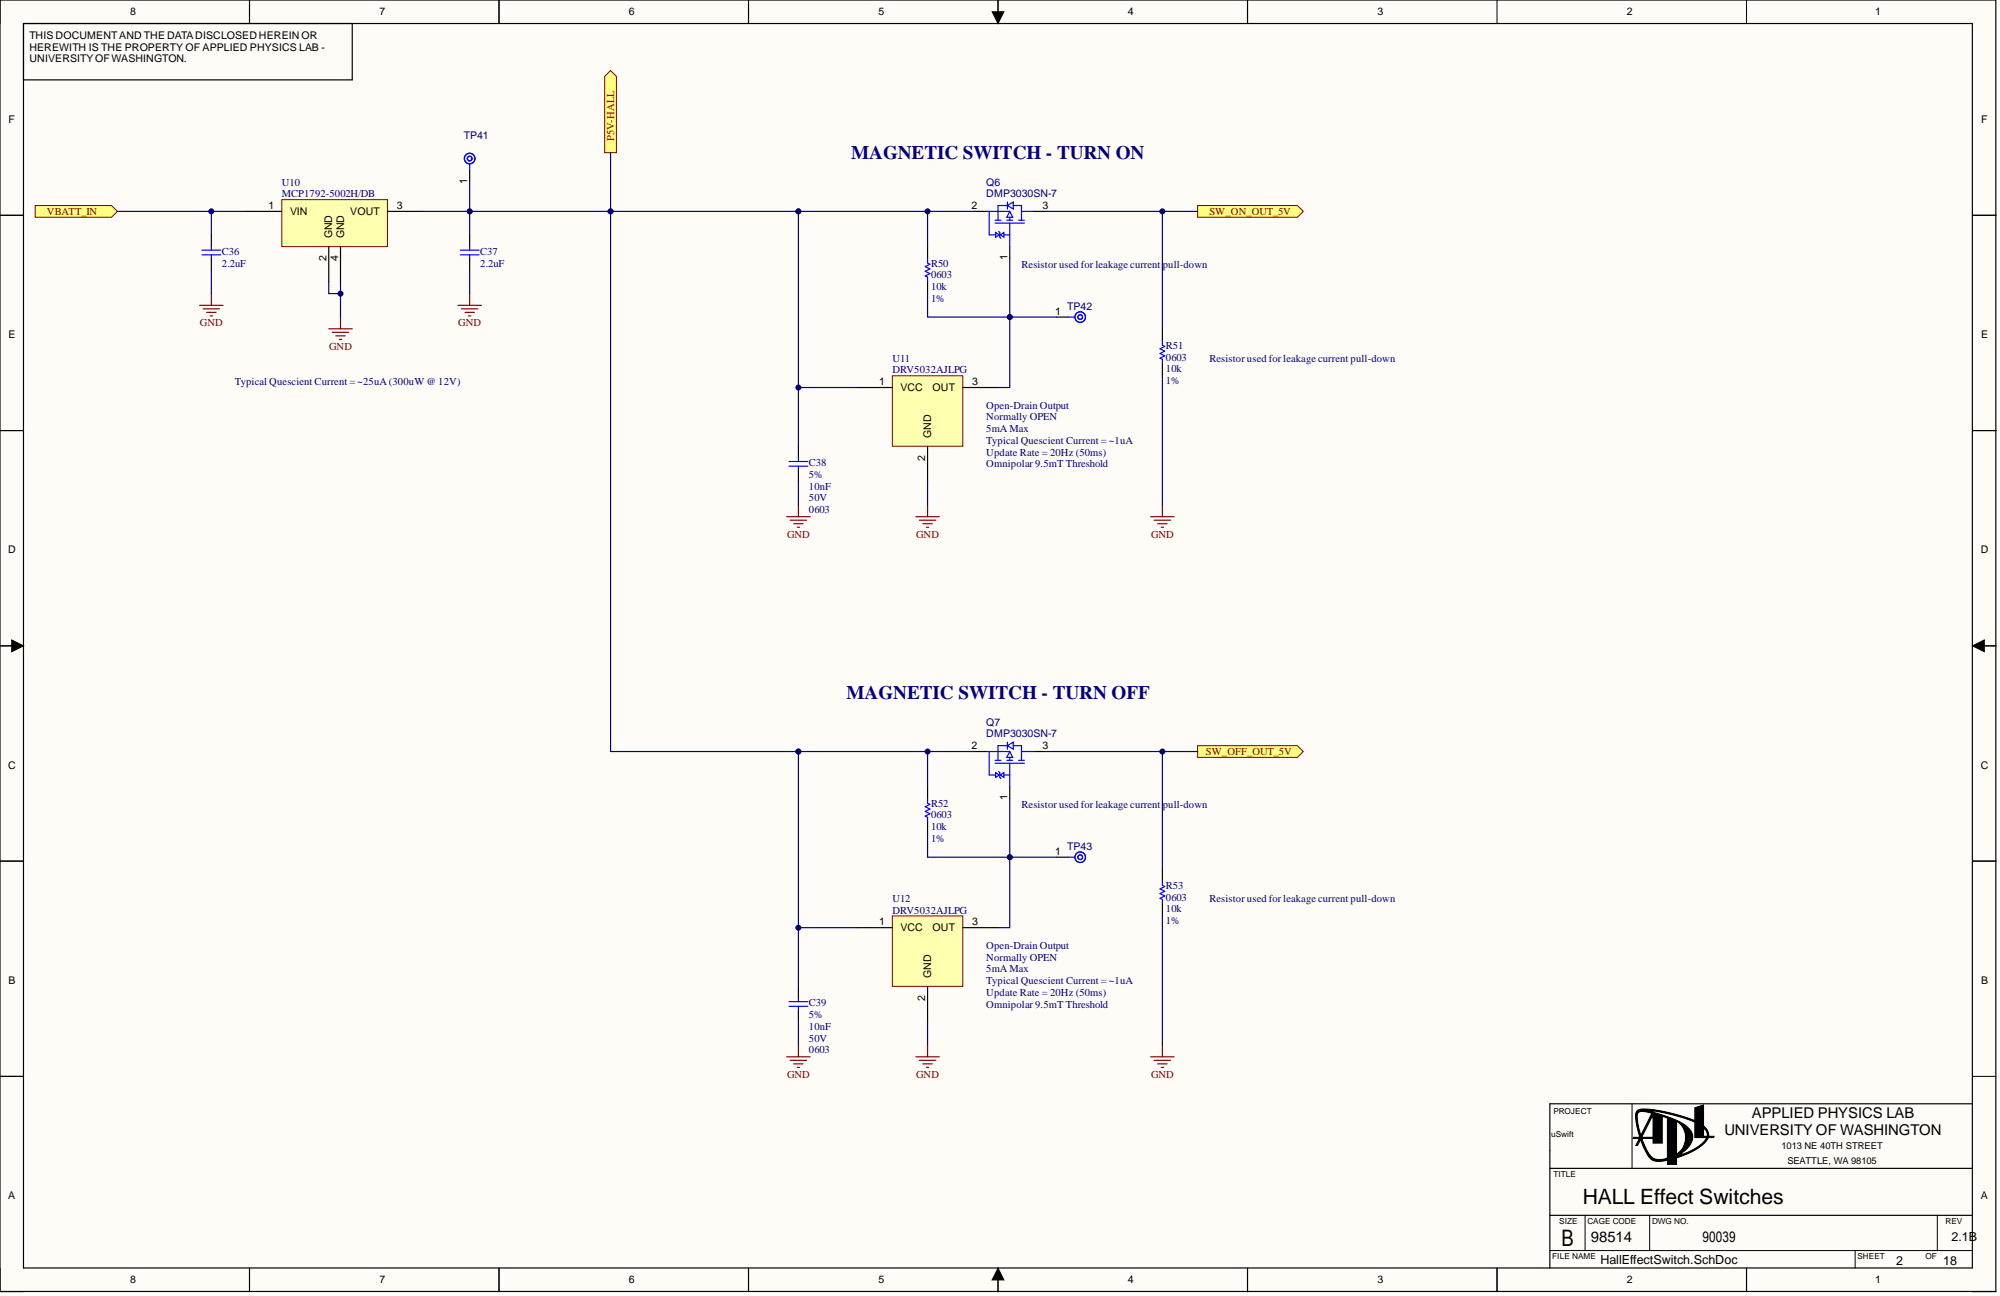
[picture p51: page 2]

THIS DOCUMENT AND THE DATA DISCLOSED HEREIN OR
HEREWITH IS THE PROPERTY OF APPLIED PHYSICS LAB -
UNIVERSITY OFWASHINGTON.

MAGNETIC SWITCH - TURN ON

Resistor used for leakage current pull-down

MAGNETIC SWITCH - TURN OFF

SIZE B | | DWG NO. 90039

FILE NAME HallEffectSwitch.SchDoc | SHEET OF 2 18

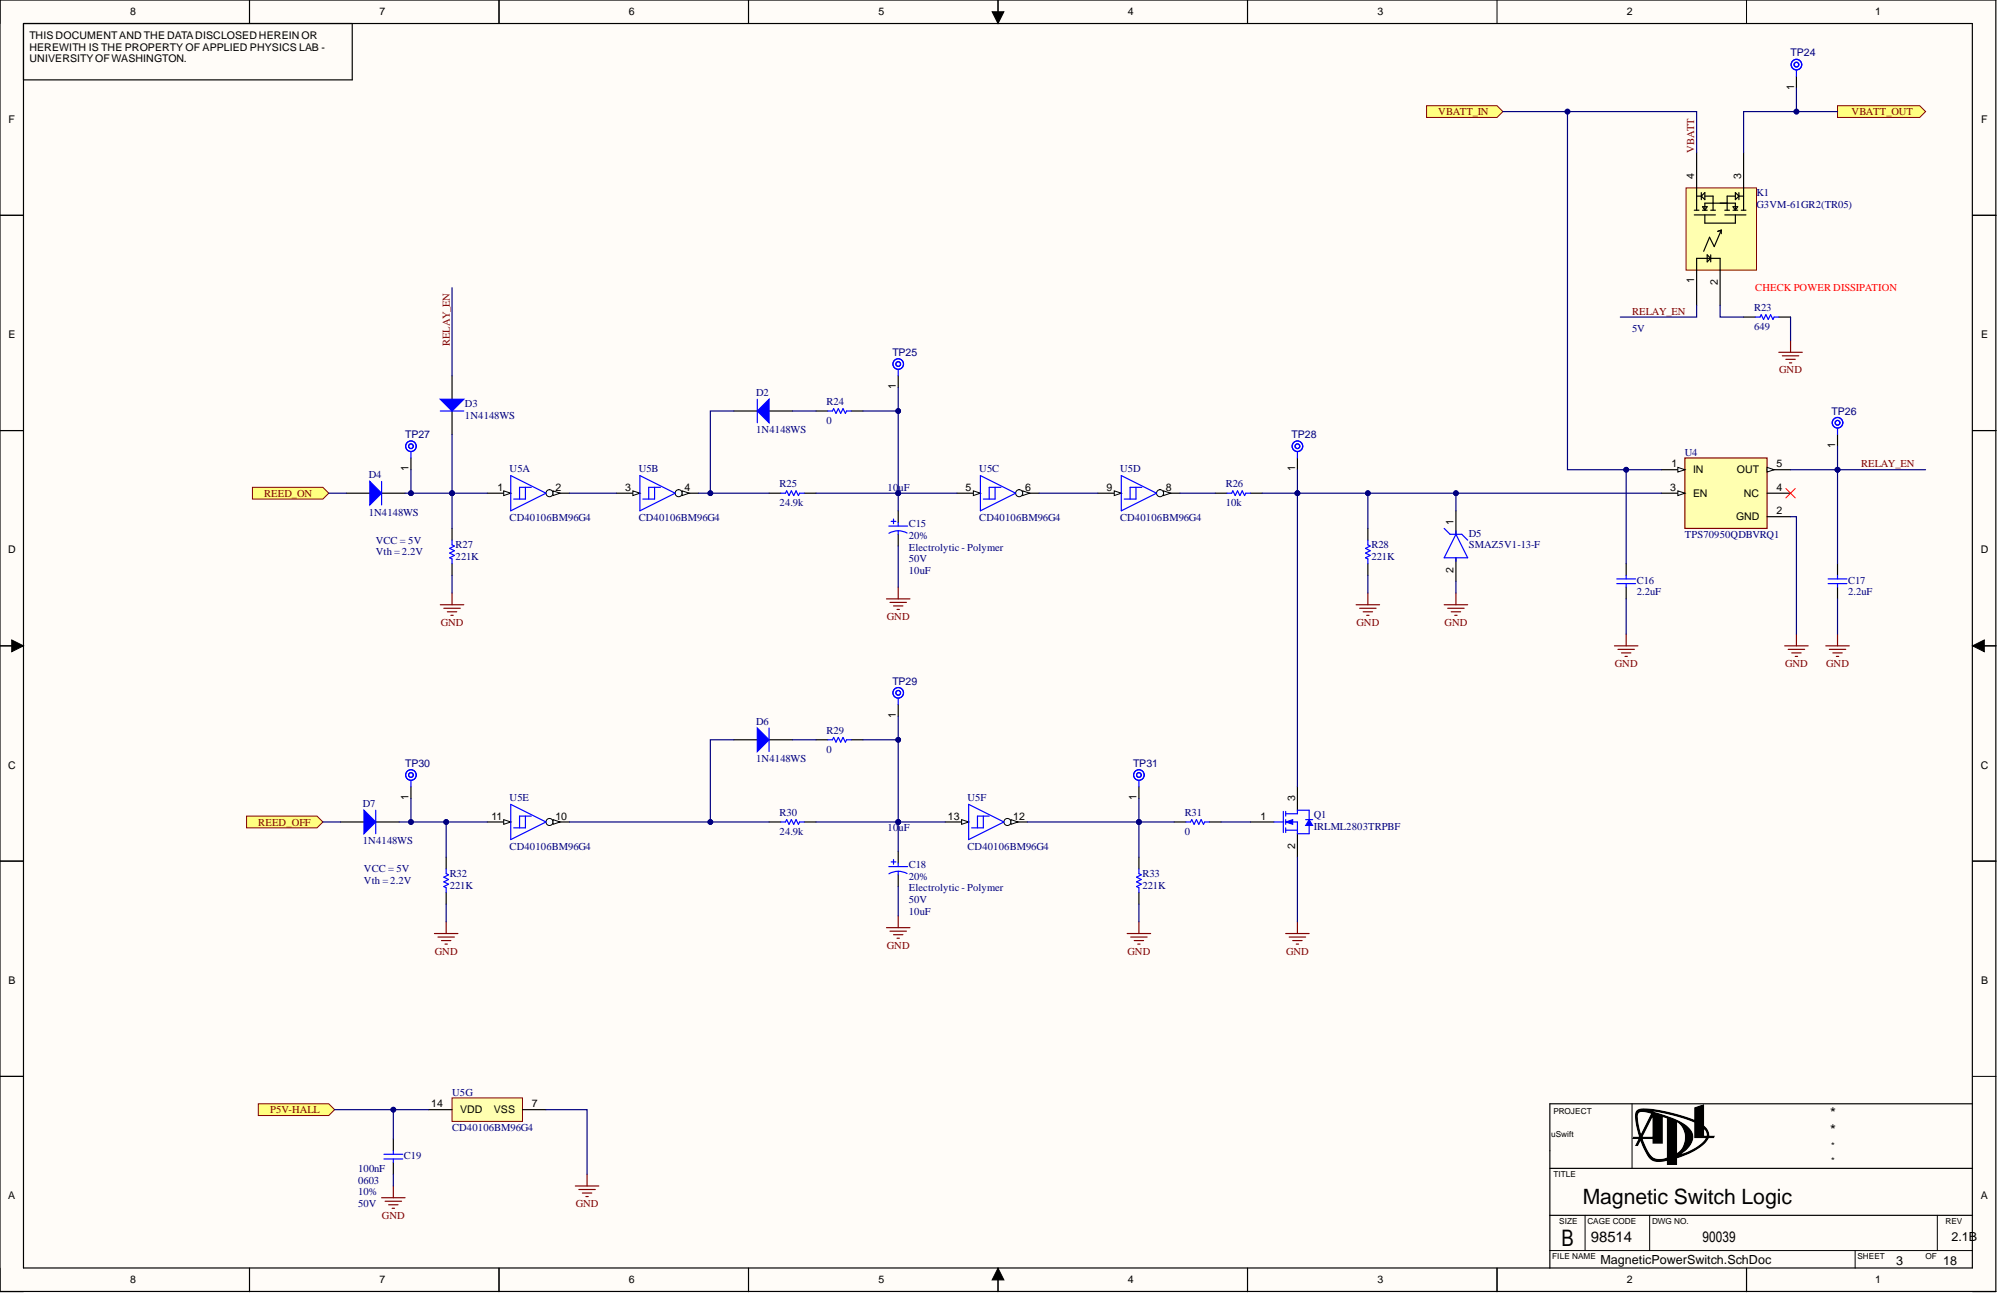
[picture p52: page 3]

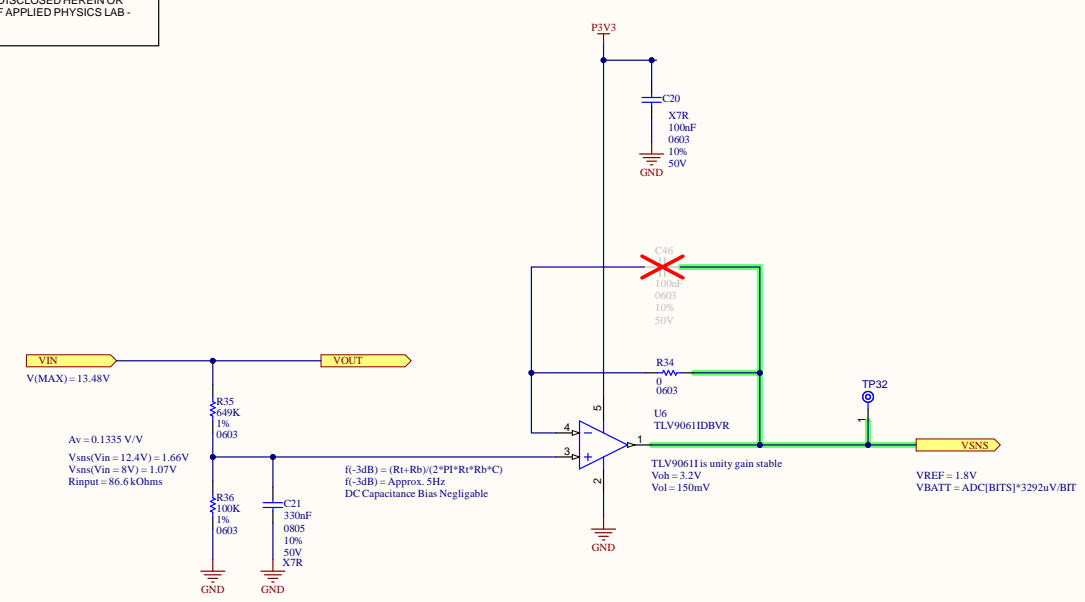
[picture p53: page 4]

f(-3dB) = Approx. 5Hz
DC Capacitance Bias Negligable

TLV9061I is unity gain stable
Voh = 3.2V
Vol = 150mV

VREF = 1.8V
VBATT = ADC[BITS]*3292uV/BIT

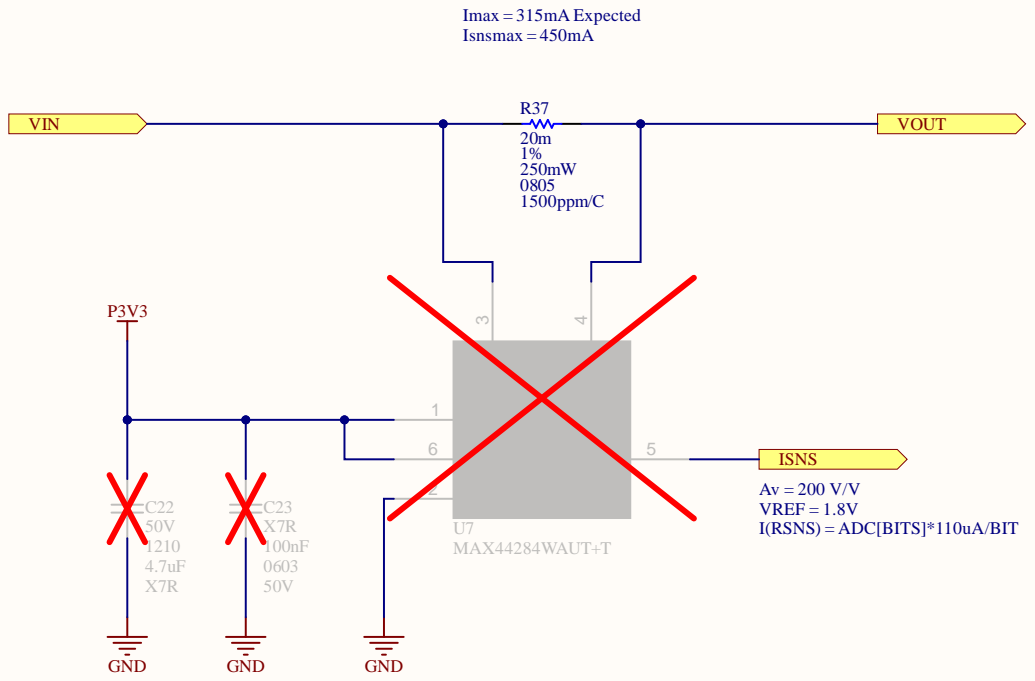
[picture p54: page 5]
Current Sense; VDD 1; GND 2; Imax = 315mA Expected Isnsmax = 450mA

RS- 4 OUT 5 SHDN 6

ISNS
VREF = 1.8V
I(RSNS) = ADC[BITS]*110uA/BIT

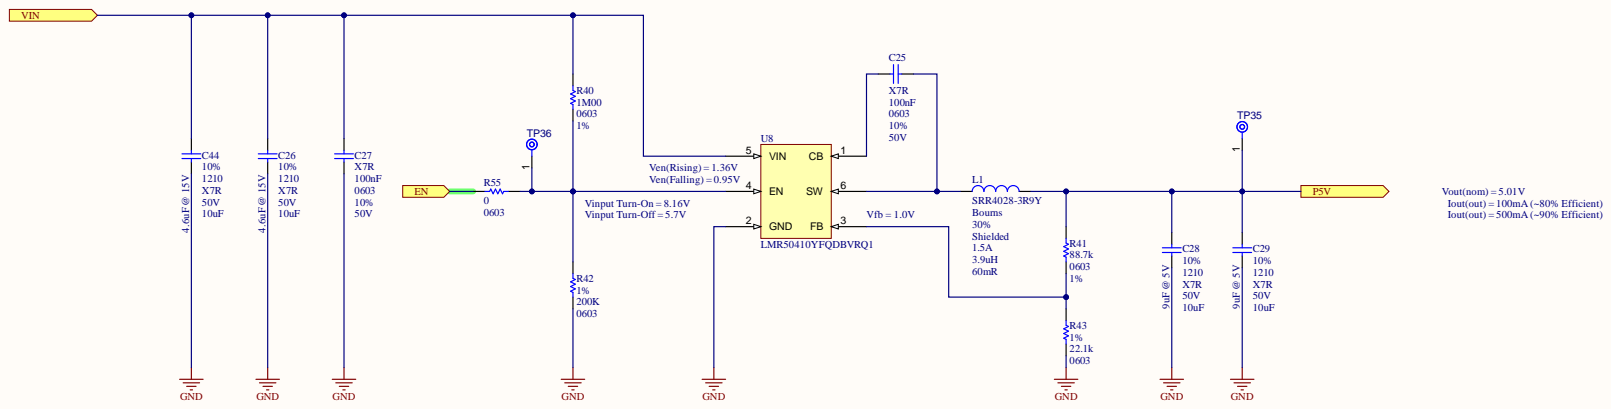
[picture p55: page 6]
HE PROPER; TY OF APPLIED PHYSI; CS LAB -; 90039 P5V_Regulator.SchDoc; APPLIED PHYSI; CS LAB; Vfb =; n = urn-Off =

TITL
P5V DC/DC Converter

SIZE | | DWG NO .

FILE NAM E | SHEET O F 6 18

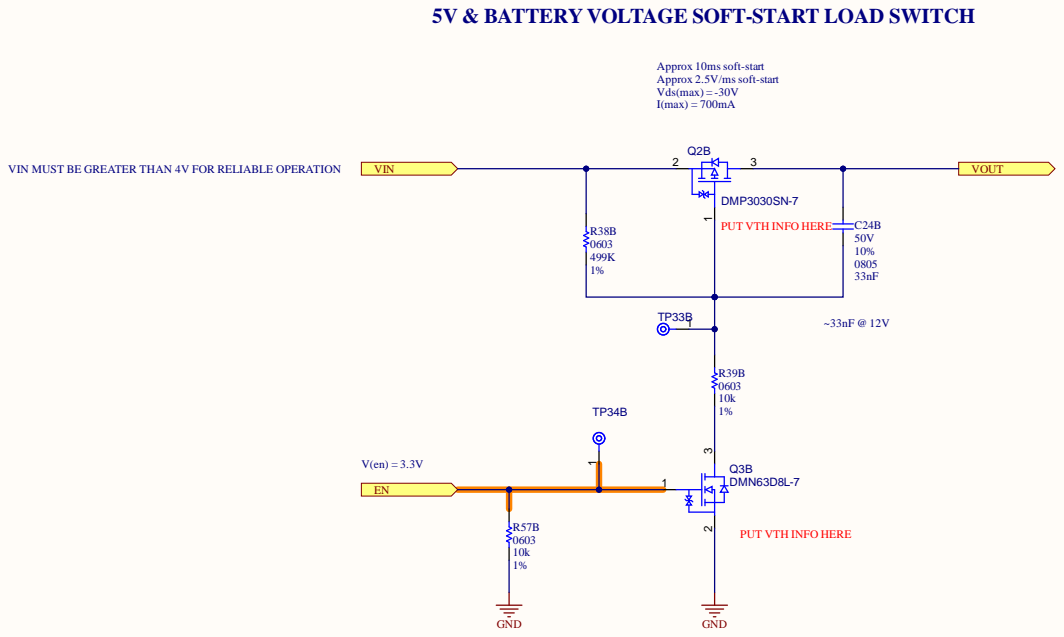
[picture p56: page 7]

5V & BATTERY VOLTAGE SOFT-START LOAD SWITCH

VIN MUST BE GREATER THAN 4V FOR RELIABLE OPERATION

PIQ3B02
PUT VTH INFO HERE

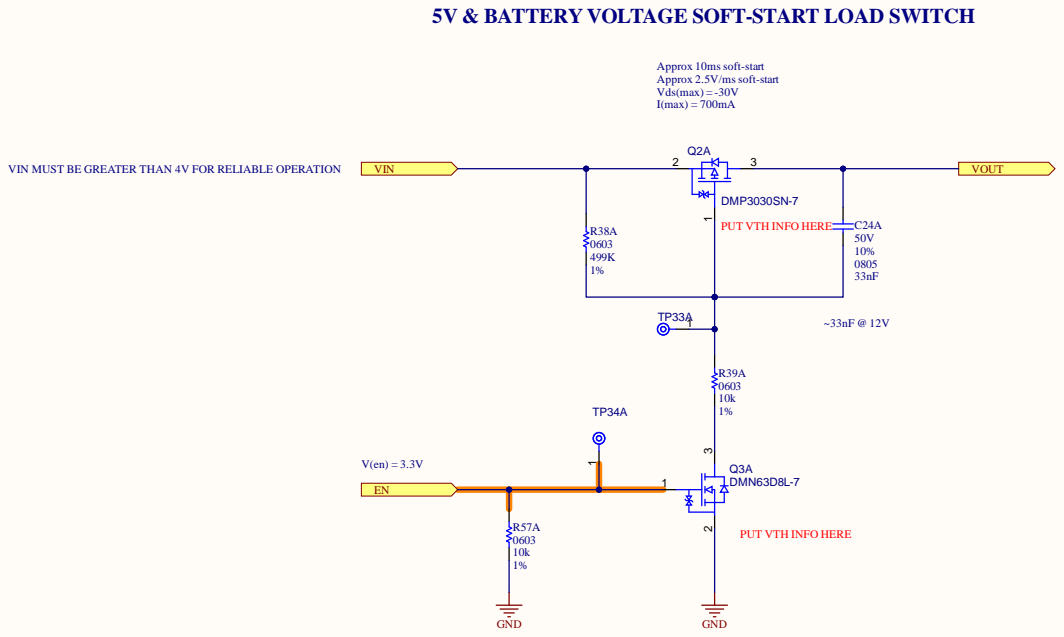
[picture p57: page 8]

5V & BATTERY VOLTAGE SOFT-START LOAD SWITCH

VIN MUST BE GREATER THAN 4V FOR RELIABLE OPERATION

PIQ3A02
PUT VTH INFO HERE

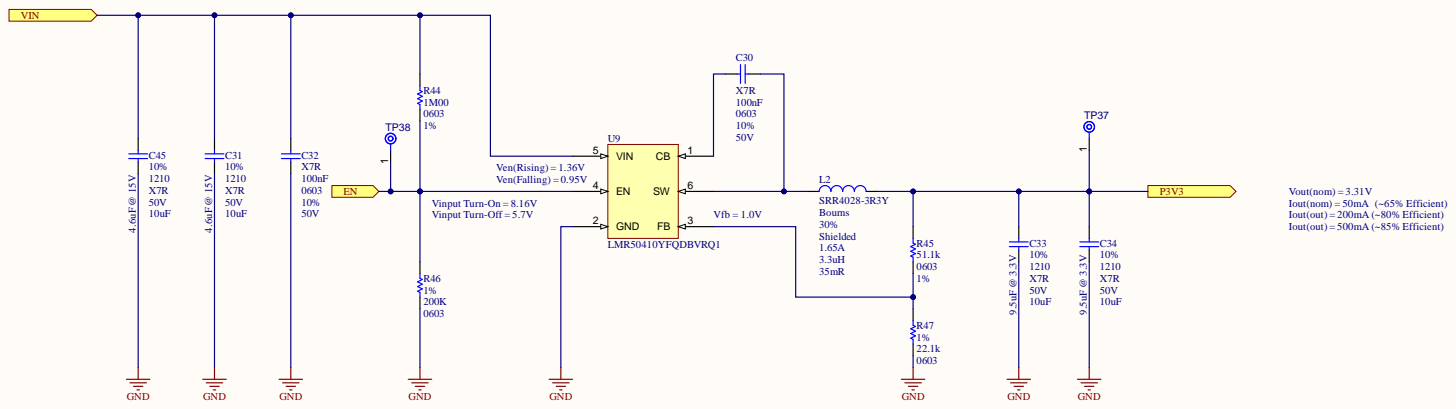
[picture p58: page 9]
HE PROPER; TY OF APPLIED PHYSI; CS LAB -; 90039 P3V3_Regulator.SchDoc; APPLIED PHYSI; CS LAB; Vfb =; n = urn-Off =

TITL
P3V3 DC/DC Converter

SIZE | | DWG NO .

FILE NAM E | SHEET O F 8 18

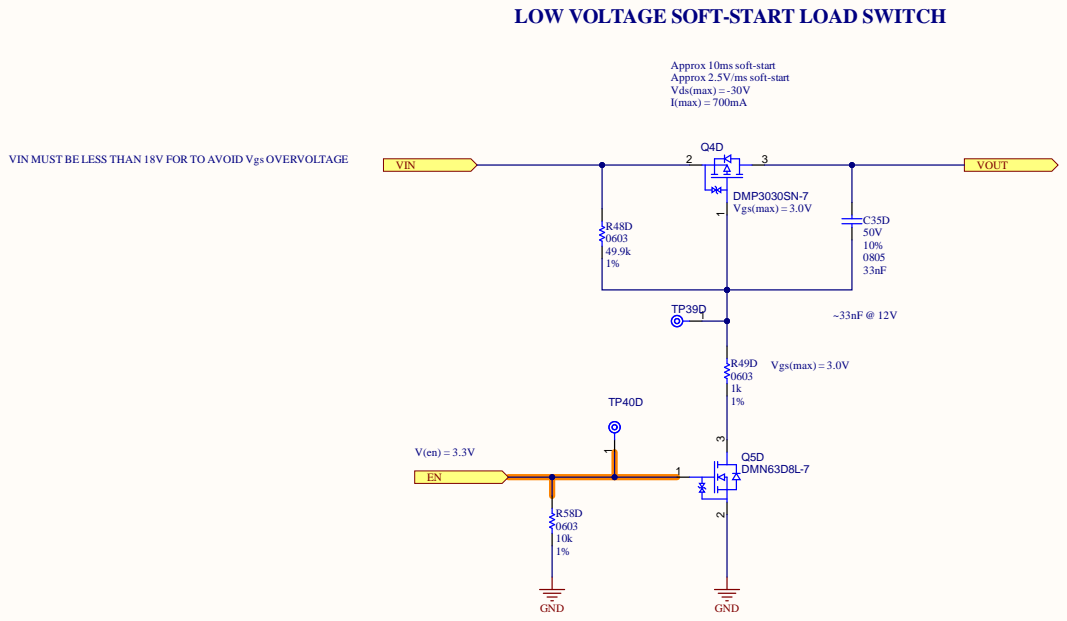
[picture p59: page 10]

LOW VOLTAGE SOFT-START LOAD SWITCH

VIN MUST BE LESS THAN 18V FOR TO AVOID Vgs OVERVOLTAGE

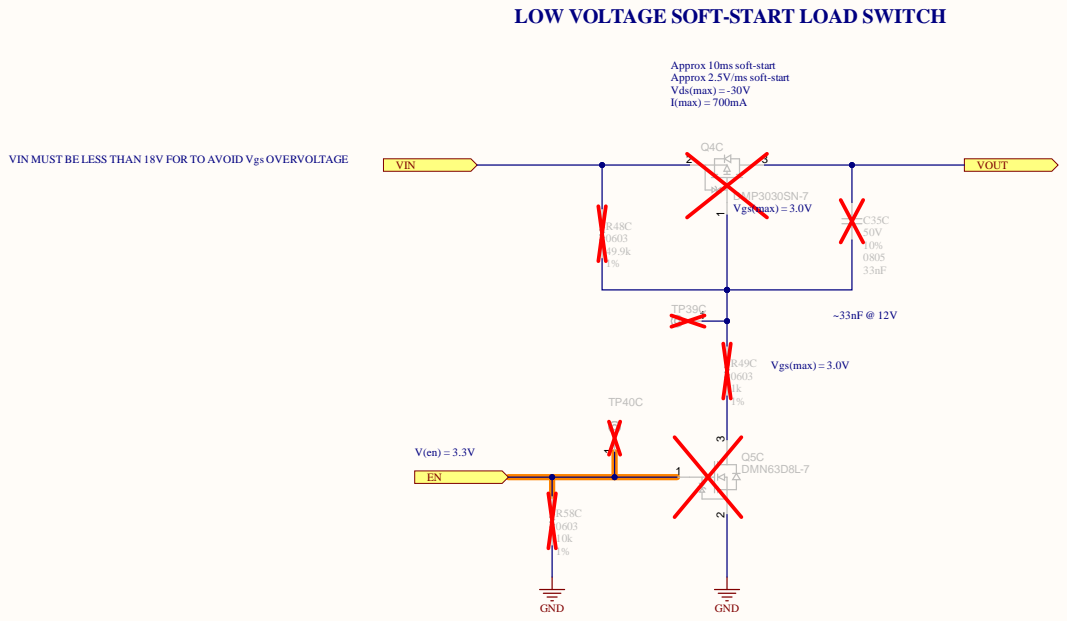
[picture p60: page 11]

LOW VOLTAGE SOFT-START LOAD SWITCH

VIN MUST BE LESS THAN 18V FOR TO AVOID Vgs OVERVOLTAGE


LOW VOLTAGE SOFT-START LOAD SWITCH

VIN MUST BE LESS THAN 18V FOR TO AVOID Vgs OVERVOLTAGE


LOW VOLTAGE SOFT-START LOAD SWITCH

VIN MUST BE LESS THAN 18V FOR TO AVOID Vgs OVERVOLTAGE

ALWAYS ON

3.3V DC/DC Converter
P3V3_Regulator.SchDoc
VIN

5V DC/DC Converter
P5V_Regulator.SchDoc

ALLOWS DISABLE FOR
DEEP SLEEP POWER SAVING

TITLE
Power Converter Main

VINPUT VIN; VOUT; RS232 TO UART; GND MCU-RS-232-RXD; VIN VOUT

CT POWER SWITCH
PowerSwitch_P12V.SchDoc

POVBATT0PWRIN
VBATT_PWRIN
NLCT0SENSOR0HARNESS0CT0PWR0EN
CT-SENSOR-HARNESS.CT-PWR-EN

CT RS232 POWER SWITCH
PowerSwitch_P3V3.SchDoc

MCU-RS-232-TXD

MCU-RS-232-RXD

NLCT0SENSOR0HARNESS POCT0SENSOR0HARNESS
MCU-RS-232-TXD CT-SENSOR-HARNESS CT-SENSOR-HARNESS
POCT0SENSOR0HARNESS POCT0SENSOR0HARNESS0\U\A\R\T\0\F\O\R\C\E\O\F\F\ POCT0SENSOR0HARNESS0\U\A\R\T\0\I\N\V\A\L\I\D\ POCT0SENSOR0HARNESS0CT0PWR0EN POCT0SENSOR0HARNESS0MCU0UART0RXD POCT0SENSOR0HARNESS0MCU0UART0TXD

RS232_TXD CT-SENSOR-HARNESS

TITLE
CT Sensor PWR/Interconnect


SIZE | | DWG NO .

FILE NAM E RS232toUA R T.SchDoc | SHEET O F 12 18

VCC 8; VCC RF 14; RESET 9; SAFEBOOT 18; LNA EN 13; V BCKP 6; VIO SEL 15; Active antenna not supported in this design; I2C not supported in this design; VIN VOUT

GNSS-EXTINT
GNSS-PWR-EN
GNSS-TIMEPULSE

GPS POWER SWITCH
PowerSwitch_P3V3.SchDoc

No bulk capacitance needed per Integration Manual

3.3V single supply design requires VIO_SELto be OPEN

Internal pullups - OK to float externally

Active antenna not supported in this design

Iridium Modem; VIN VOUT; PIP1010 NLGND; PIP109; NLMCU0RXD POIRIDIUM0HARNESS POIRIDIUM0HARNESS0IRIDIUM0PWR0EN POIRIDIUM0HARNESS0IRIDIUM0CTS POIRIDIUM0HARNESS0IRIDIUM0RTS POIRIDIUM0HARNESS0MCU0IRIDIUM0RXD POIRIDIUM0HARNESS0MCU0IRIDIUM0TXD POIRIDIUM0HARNESS0NETWORK0AVAILABLE POIRIDIUM0HARNESS0RING0INDICATOR POIRIDIUM0HARNESS0SLEEP0CONTROL

MODEM POWER SWITCH
PowerSwitch_P12V.SchDoc
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

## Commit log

2025-01-23 Add PCB related files
    [BOM_Flight Variant.csv, CTSensor.SchDoc, ExternalRam.SchDoc, GPS.SchDoc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]
2025-01-24 publish v2.1 Bill of Materials
2025-01-24 commit 3d print files
    [Antenna Mount, microSWIFT v2 13Aug2024_LargeHex.STL, Bulkhead Support, microSWIFT v2, Top.STL, Bulkhead Support, microSWIFT, v2, Middle.STL, Bulkhead support, 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]
2025-02-27 Add PCB files, STL files, and exploded view
    [Antenna Mount, microSWIFT v2 13Aug2024_LargeHex.STL, BOM_Flight Variant.csv, Bulkhead Support, microSWIFT v2, Top.STL, Bulkhead Support, microSWIFT, v2, Middle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]
2025-02-28 Create microSWIFT Assembly, Short.PNG
